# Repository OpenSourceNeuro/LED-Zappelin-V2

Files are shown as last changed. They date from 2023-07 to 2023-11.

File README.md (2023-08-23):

<p align="left">
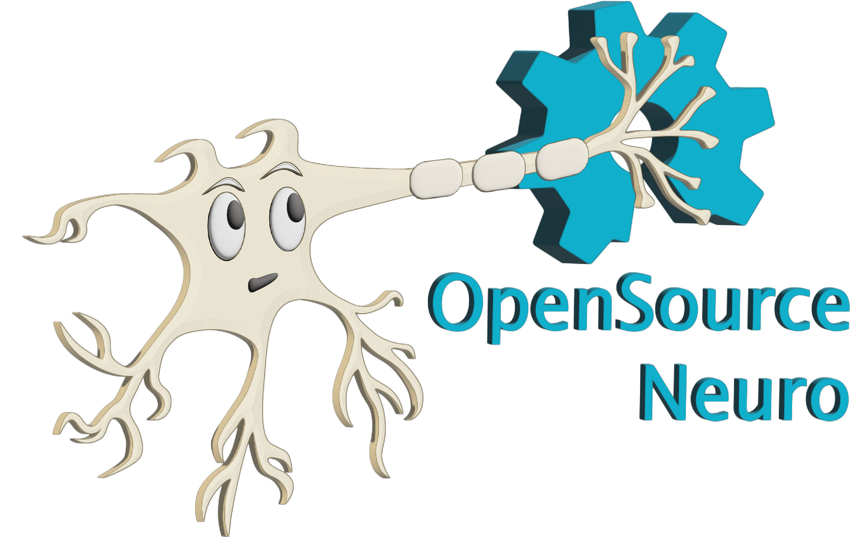
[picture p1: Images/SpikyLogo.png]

</p>

<h1 align="center"> LED Zappelin' v2</h1>
<h3 align="center">  An Open Source and versatile LED controller for arbitrary spectrum visual stimulation and optogenetics during two-photon imaging.</h3></p>
<h6 align="right">developed by M.J.Y. Zimmermann, A.M. Chagas & T. Baden</h6>

<br>

This project is licensed under the <a href="https://www.gnu.org/licenses/gpl-3.0.html">GNU General Public License v3.0</a>
<br>
The hardware is licensed under the <a href="https://cern-ohl.web.cern.ch">CERN OHL v1.2</a>

***

<p style='text-align: justify;'>
Two-photon microscopy is a cornerstone technique in neuroscience research, but combining this technology with spectrally arbitrary light stimulation can be challenging due to crosstalk between stimulation light and fluorescence detection. To overcome this limitation, we present LED Zappelin': a simple and low-cost electronic solution to rapidly time-interleave stimulation and detection epochs during scans.
</p>

The second version of this project allows user to either:

  - Independently drive up to 24 arbitrary spectrum LEDs to meet user requirements. Using the <a href="https://www.ti.com/lit/ds/symlink/tlc5947.pdf">TLC5947 LED driver</a>.
  - Control external light source generator such as the <a href="https://www.thorlabs.com/newgrouppage9.cfm?objectgroup_id=13597">Thorlabs Chrolis</a>. Using TTL logic circuits.

</br>

<p align="center">
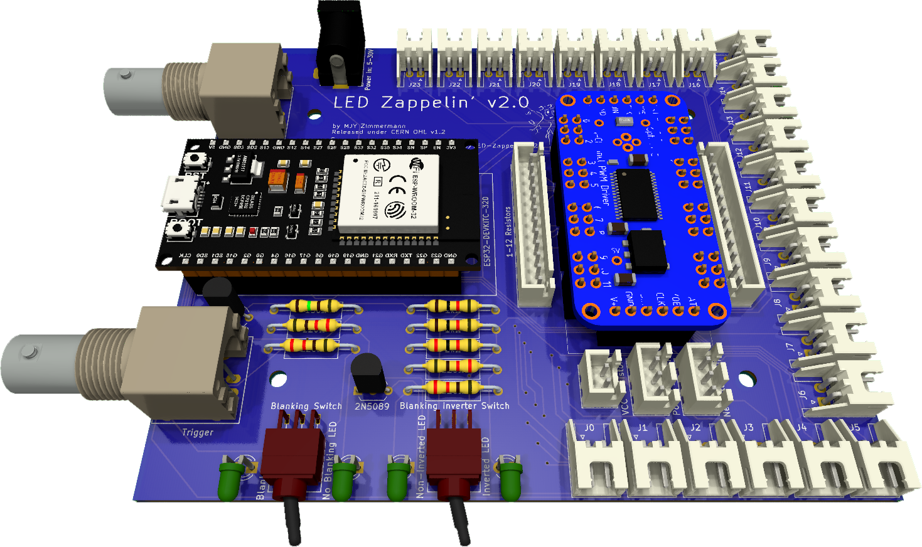
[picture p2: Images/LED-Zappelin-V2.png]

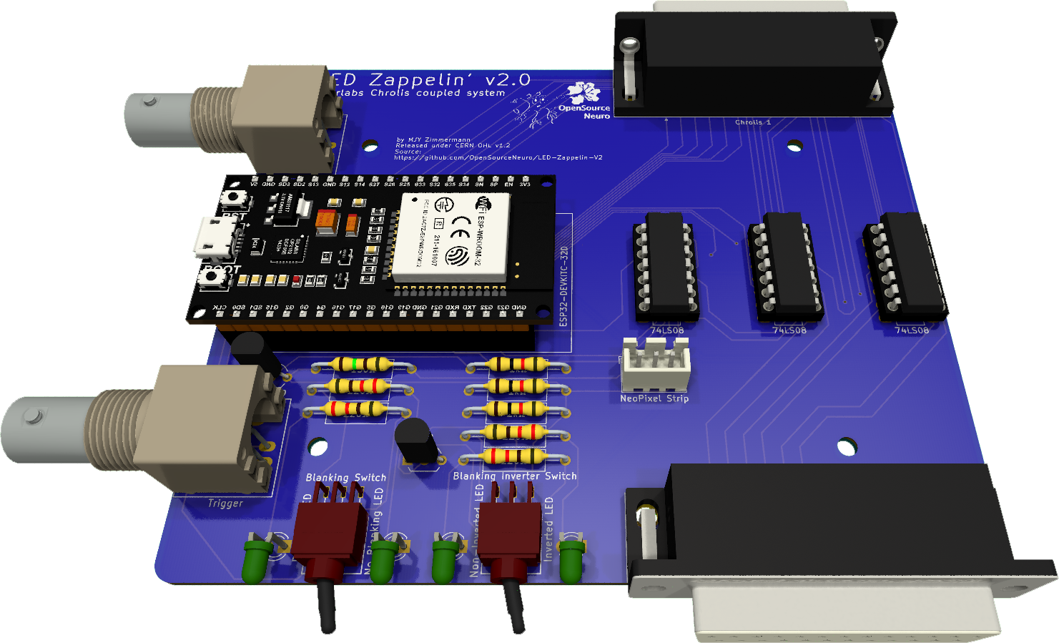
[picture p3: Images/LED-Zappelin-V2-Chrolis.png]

</p>

<h5 align="justify"> <em>Left: </em>LED Zappelin' mounted with a TLC 5947 controlling up to 24 LED channels. <em>Right: </em>LED Zappelin' mounted with TTL circuit controlling two 6-High_Power LED Chrolis systems</h5>

<br></br>

<p style='text-align: justify;'>
In the <a href=https://pubmed.ncbi.nlm.nih.gov/35498254/>original publication</a>, we demonstrate the utility of our stimulator for colour vision experiments on the in vivo tetra-chromatic zebrafish retina and for optogenetic circuit mapping in Drosophila.
</p>

<br>

- [Introduction](#Introduction)
- [BoM](https://github.com/BadenLab/LED-Zappelin/blob/master/Bills%20of%20Materials/BOM%20-%20Stimulator.csv)
- [Request a Quote]()
- [A stimulator for visual neuroscience](#Colour-Vision-Experiment)
- [A stimulator for optogenetics](#Optogenetics-Experiment)
- [A detailed assembly and instruction manual](https://github.com/BadenLab/LED-Zappelin/blob/master/Instruction%20Manual/README.md)
- [A step by step calibration script](https://github.com/BadenLab/LED-Zappelin/blob/master/Instruction%20Manual/Stimulator%20Calibration/Stimulator_Calibration.ipynb)
- [Repository Structure](#Repository-Structure)

<br>

## Introduction

<p align="justify">
Combining two-photon imaging with additional light stimulation – for example for visual stimulation or for driving optogenetic actuators – has remained challenging because the stimulation light can interfere with fluorescence detection. This can result in light artefacts in the image and/or may damage sensitive fluorescence detection equipment (e.g. photomultiplier tubes, PMTs).
</p>

<p align="justify">
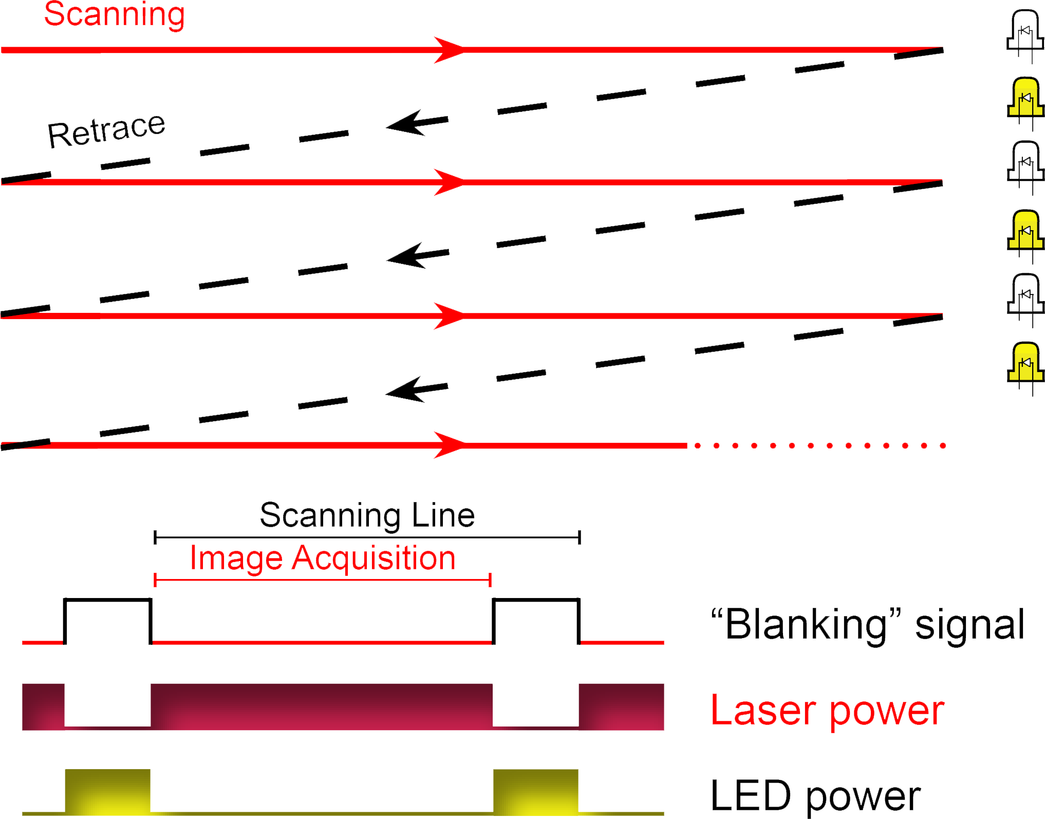
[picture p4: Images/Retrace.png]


A temporal separation between light stimulation and fluorescence detection, for example during the scan-retrace, can ameliorate these problems.
This problem can be readily solved electronically, for example through use of a microcontroller.
</p>

<br>

<p align="justify">
Here, we present such a solution. Our system can either line-synch up to 24 independent LED channels or can be connected to external commercial light sources, and can be assembled from off-the-shelf components for substantially below $200. This provides for flexible options of spectrally diverse light stimulation during two-photon scanning and comfortably provides sufficient power to drive standard optogenetics actuators such as CsChrimson.
</p>

<br>

<p align="justify">
Alongside, we also provided <a href="https://github.com/OpenSourceNeuro/LED-Zappelin-V2/tree/main/Casing%20Files">custom casing files</a> (for either 3d print or laser-cut), <a href="https://github.com/OpenSourceNeuro/LED-Zappelin-V2/tree/main/3D%20files">designed suggestions</a> for optically combining LED banks using Thorlabs parts, and an alternative 3D-printed LED holder and microscope chamber.
</p>

<p align="justify">
The device is built around an <a href="https://www.espressif.com/en/products/socs/esp32">ESP32</a>, a microcontroller which exchange signals with the recording setup, drive the light sources and runs on C++. However, users do not need to interfere with the source code as we provide an intuitive and interactive <a href="">Graphical User Interface</a> (GUI), from which all functions and variables can be manipulated.
</p>

</br>

<p align="center">
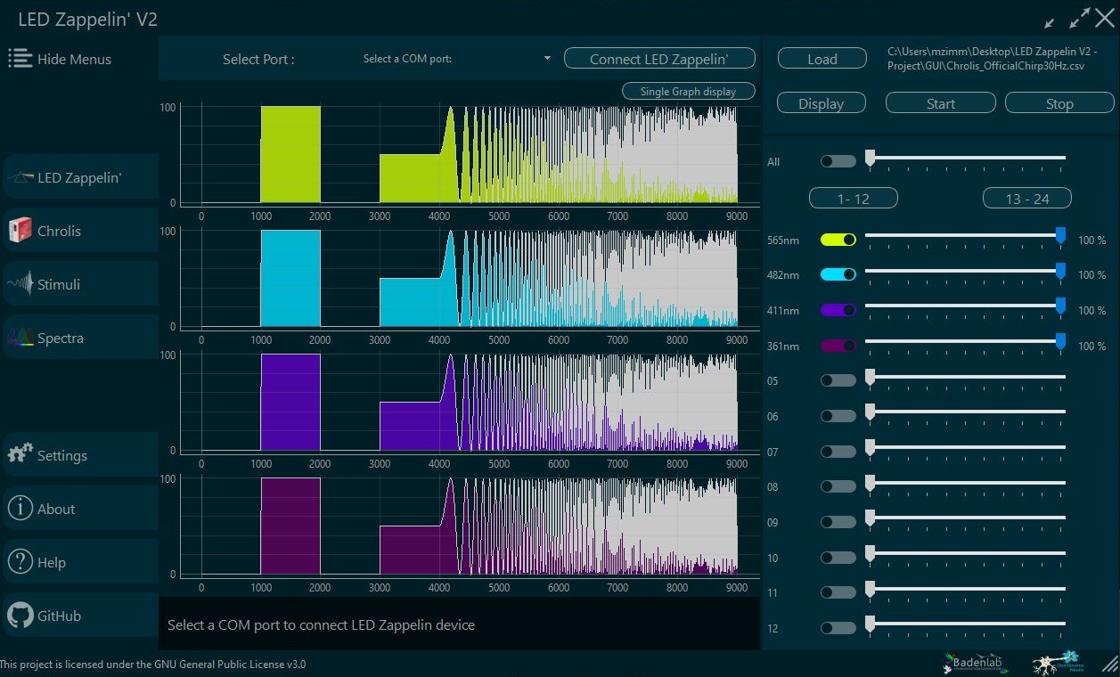
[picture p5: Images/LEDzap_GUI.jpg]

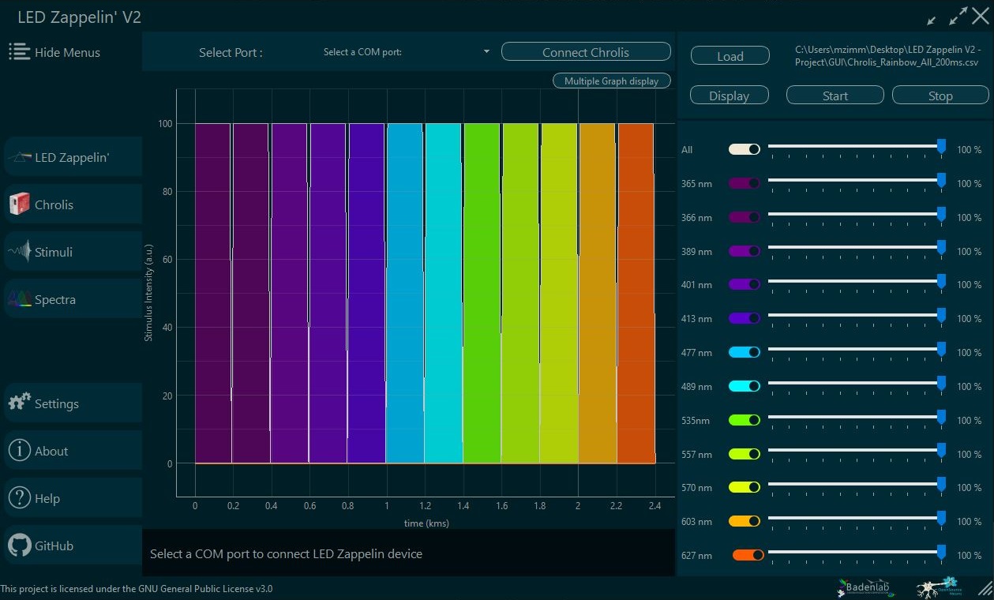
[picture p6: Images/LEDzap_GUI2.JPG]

</p>

<h5 align="justify"> <em>Left: </em>LED Zappelin' GUI controlling 4 LEDs, all executing a chirp stimulus. <em>Right: </em>LED Zappelin' controlling 12 LED channels from two Chrolis systems, executing successive On/Off stimulati</h5>

<br></br>

<p align="justify">
<a href="https://github.com/OpenSourceNeuro/LED-Zappelin-V2/blob/main/GUI_UserManual.md"><strong>Here</strong></a>, is the full user guide documentation.
</p>

<br>

***

## Colour Vision Experiment

Demo CountPages alpha (https://youtu.be/FhLoFGbbpPo)

<p align="justify">
We used LED Zappelin' for studying the retinal processing of the tetra-chromatic zebrafish retina in response to multichromatic signal.
Here we selected four LEDs that match the peak sensitivities of each cone opsins of our model.
We chose LEDs and band pass filters in such manner that the stimulating light and the detection bands do not overlap as much as possible. However a temporal separation is still necessary to avoid some overlapping and any light artefact.
</p>

</br>

<p align="center">
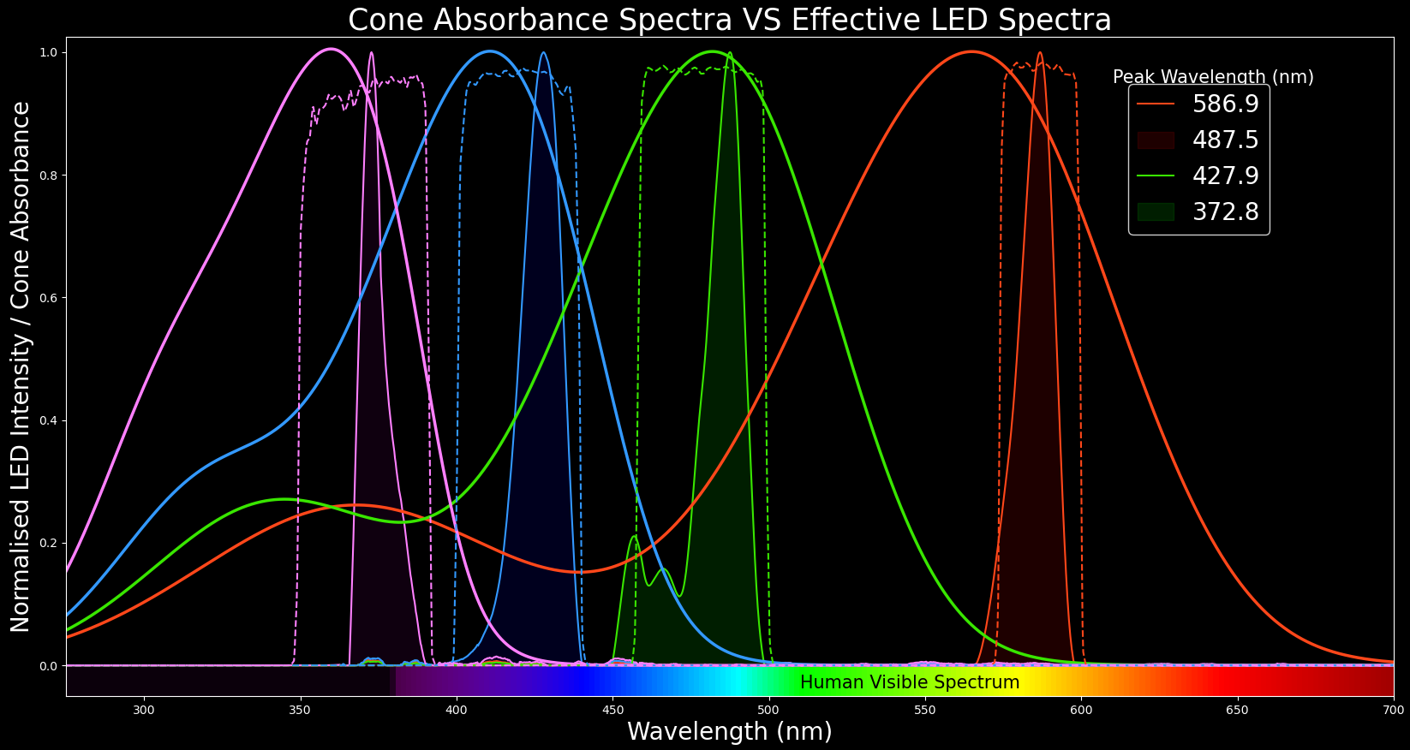
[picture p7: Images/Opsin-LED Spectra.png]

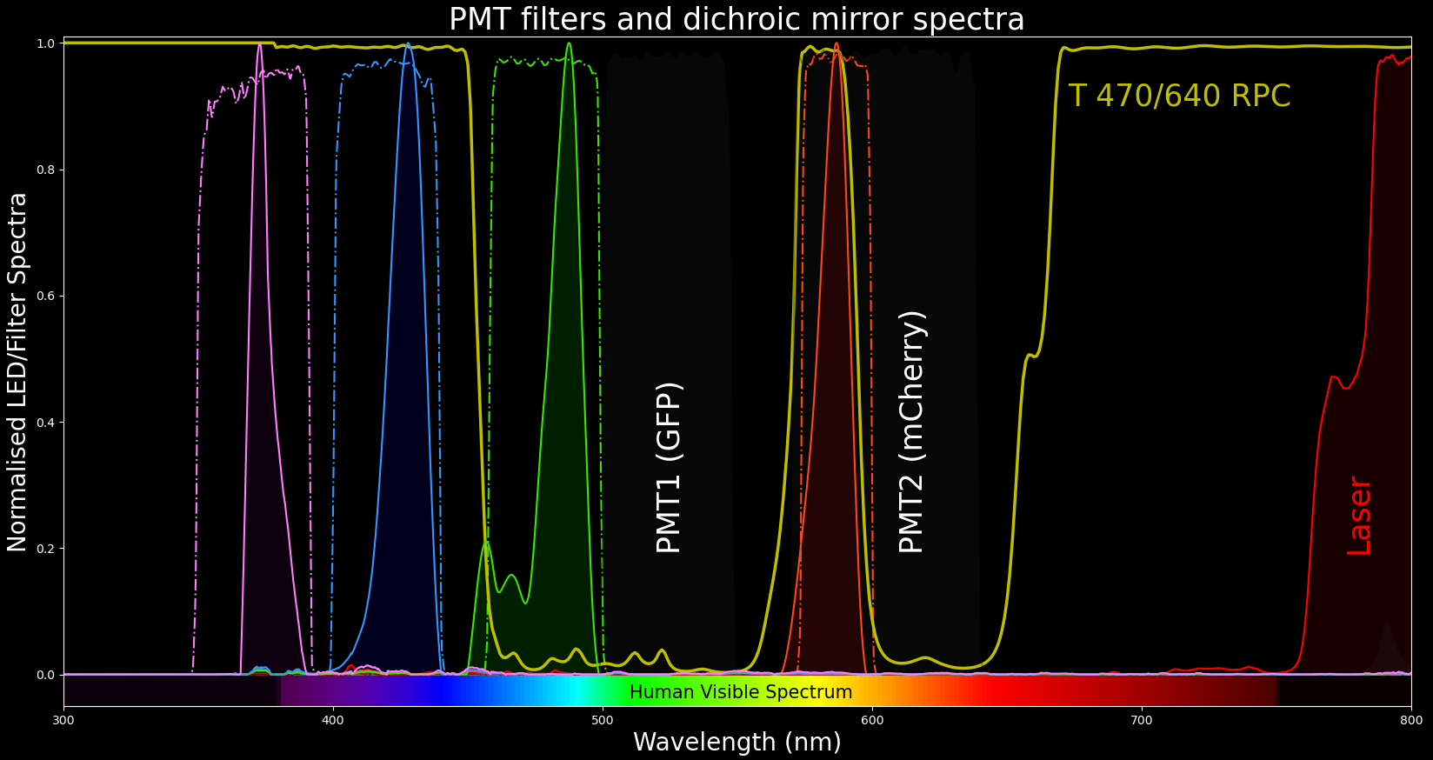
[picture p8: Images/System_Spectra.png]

</p>

<h5 align="justify"> <em>Left: </em>Zebrafish's opsin absorbance spectra overlapped with four filtered LED spectra. <em>Right: </em>The four selected stimulation LEDs along the microscope setup spectra features</h5>

<br></br>

<p align="justify">
 We recorded light-driven calcium signals under 2-photon from <a href="https://pubmed.ncbi.nlm.nih.gov/29937350/"> retinal bipolar cells in vivo in the tetra-chromatic larval zebrafish</a>. We used a transgenic line expressing a genetically encoded biosensors for calcium at the  bipolar cell synaptic terminals level (ctbp2:SyGCaMP6)  within the inner plexiform layer (IPL).
</p>

<p align="justify">
Following <a href="https://pubmed.ncbi.nlm.nih.gov/2321027/">established protocols</a>, we used a Sutter MOM microscope where light stimulation is displayed through the objective directly onto the fish retina along with the laser excitation. Fluorescence is also collected through the objective as well as from below the stage (not shown).
</p>

<p align="justify">
We presented full field steps of red, green, blue and UV light to the fish eye (respectively 567, 480, 420 and 365nm), and recorded evoked calcium signals as a readout of synaptic activity. We observed spectrally different tunings from distinct bipolar cell terminals  without detectable stimulus artefact across the scan.
</p>

<p align="center">
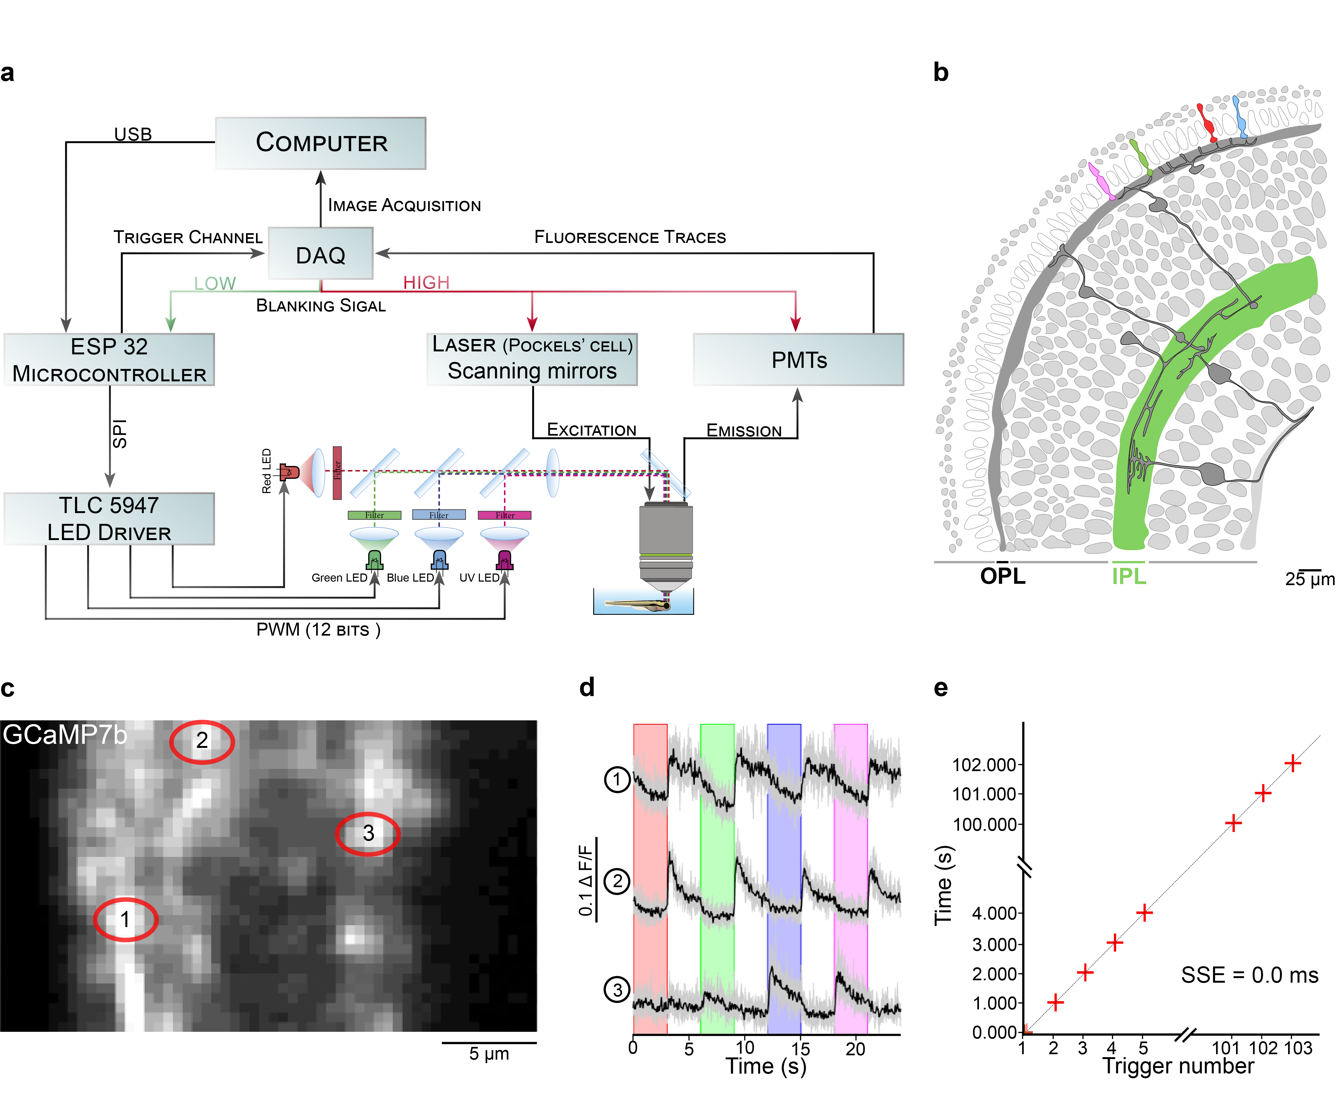
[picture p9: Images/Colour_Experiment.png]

</p>
<h5 align="justify"> a) Overview of the setup described for the visual stimulation experiment performed on the tetra-chromatic zebrafish. b) Drawing of the larval zebrafish retina highlighting the IPL. c) 2 photon scan field of the IPL with regions-of-interest marked by red circles. The 64x32 pixel image was obtained by at 1ms scan rate. d) Ca²⁺ traces (mean traces in black, n=5 trials in grey) in response to consecutive red, green, blue and UV On/Off flashes. e) Trigger timing recorded by the DAQ highlighting its accuracy over time with a precision of 0.1µs. t(n+1) = t(n) + T, where “t” is the recorded trigger time and “T” the trigger period. </5>

***

## Optogenetics Experiment

In addition to colour vision experiments, LED Zappelin' is well suited for optogenetic manipulations.

<p align="justify">
Here we illustrate this application in Drosophila larvae, were we recorded brain-wide calcium signals under 2P in response to optogenetic stimulation of all olfactory sensory neurons (OSNs).  We expressed the red-shifted channel rhodopsin CsChrimson OSNs and the genetically encoded calcium indicator GCaMP6s pan-neuronally by using larvae with the genotype: elav-Gal4;UAS-GCaMP6s/Orco-LexA;LexAOp-CsChrimson.
</p>

<p align="justify">
We placed first instar larvae under a custom-made 2P microscope in a <a href"https://github.com/OpenSourceNeuro/LED-Zappelin-V2/tree/main/3D%20files/Optogenetics%20Components">3D-printed optogenetics LED chamber</a>.
Red light stimulation was delivered from around the sides of the recording chamber and GCaMP6s fluorescence intensity was collected by two detectors one through the objective lens, and a sub-stage PMT.
We presented full field illumination steps of 615 nm light lasting 0.5 s and an inter-stimulus interval of either 3 s (b) or 10 s (c).
</p>

<p align="justify">
We observed robust stimulus-evoked activity in the primary olfactory sensory centres of the larval brain, the antennal lobes (red outlines). Similarly to colour vision experiments, we detected no light artefact.
</p>

<p align="center">
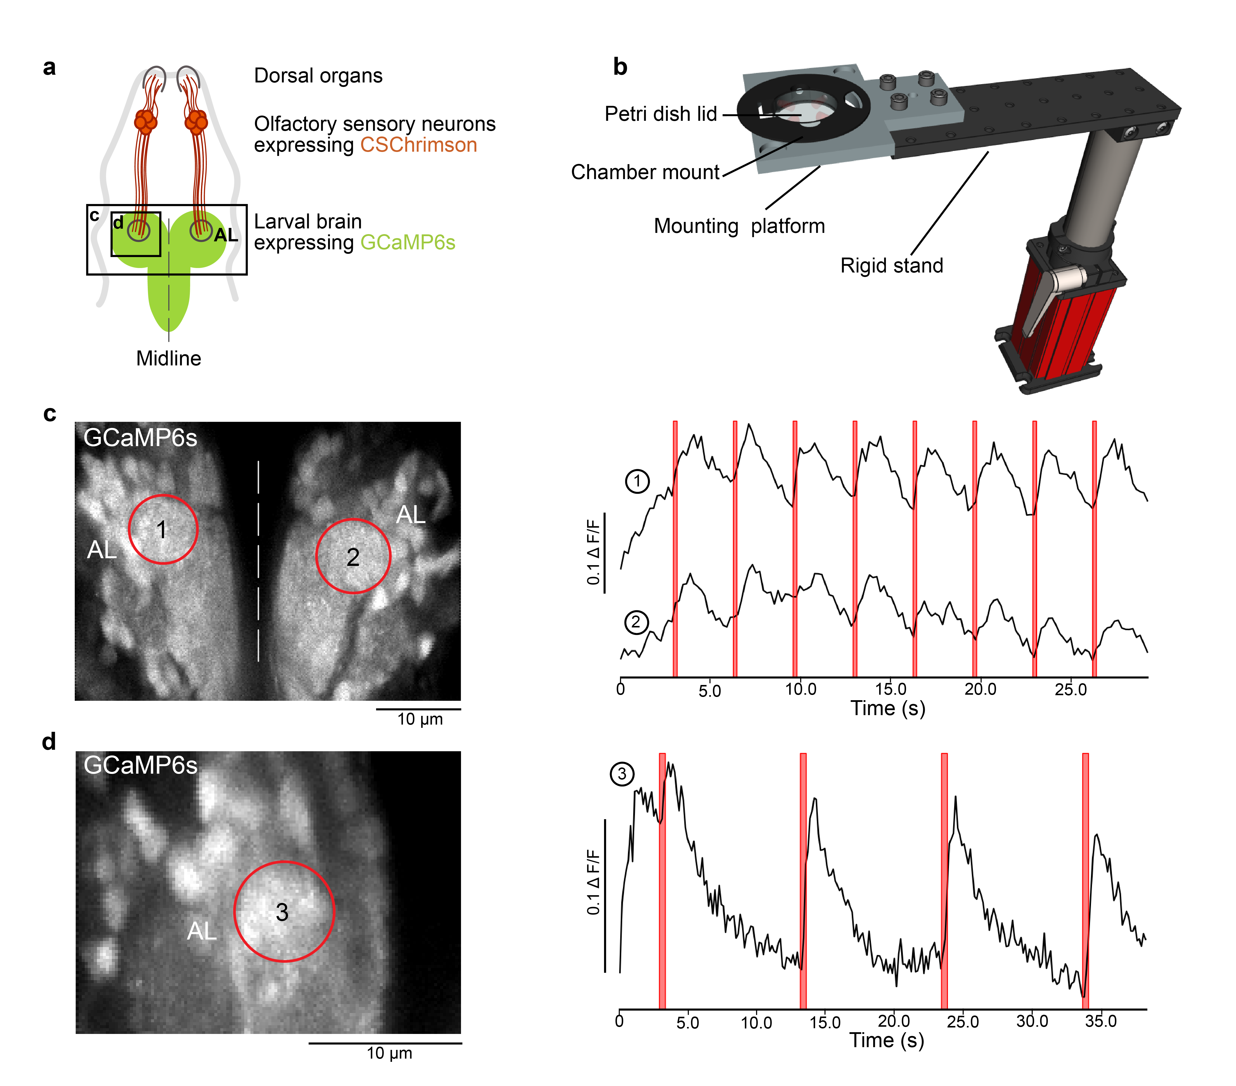
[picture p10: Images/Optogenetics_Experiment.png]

</p>
<h5 align="justify">  a) Schematic of a fruit fly first instar larval head expressing the red-shifted channel rhodopsin CsChrimson in olfactory sensory neurons and GCaMP6s in all neurons. b) Rendering of the experimental setup: The mounting chamber is placed in a 3D-printed holder, screwed onto a rigid stand (ThorLabs).  c),d)  2 photon scan field of the larval brain with antennal lobes marked by red circles (left) and Ca²⁺ traces in response to red flashes (right). c. Stimulation duration = 0.5 s, inter-stimulus interval = 3 s, image dimensions = 256 x 230, scan rate = 1081 Hz, frame rate = 4.7 Hz. d) Stimulation duration = 0.5 s, inter-stimulus interval = 10 s, image dimensions = 256 x 170, scan rate = 1077Hz, frame rate = 6.34 Hz. </h5>

***
## Repository structure (to be updated)

```
├───3D Designs                                Contains printed parts for the stimulator and optical components
│   ├───Optical Components
|   |   ├───STL renderings                    - Printing files
|   |   └───SCAD files                        - SCAD files to be modified if need be
│   ├───Optogenetics Components
|   |   ├───STL renderings                    - Printing files
|   |   └───SCAD files                        - SCAD files to be modified if need be
│   └───Stimulator
|       ├───STL renderings                    - Printing files
|       └───SCAD files                        - SCAD files to be modified if need be
|
├───Arduino Code                              Stimulator Code
|   ├───Stimulator Code                       - Adaptable C+ code for running the stimulator
|   └───LED driver library                     - Library to run the TLC 5947
|
├───Bill of Materials                         List of necessary components and retailer suggestions
|
├───Datasheets                                - Contains all technical sheet for:
|   ├───Optical Components                    - ...LEDs, Filters, Dichroic Mirrors used in the presented example
|   ├───Stimulator                            - ...micro-controller and LED driver
|   └───Spectrometer                          - ...device used for calibration
|
├───Images                                    Image repository
|
├───Instruction Manual                        Detailed manual to assemble and calibrate the stimulator
|   └───Stimulator Calibration                - Contains calibration recordings and the adaptable jupyter notebook script to calibrate the stimulator
|       ├───Arduino Calibration Code          - Sequence used for the calibration
|       ├───Calibration Figures               - Illustration from calibration measurements
|       ├───Filters                           - Filters and dicroic mirrors spectra
|       ├───Powermeter Recording              - Recording of the calibration sequence
|       ├───Spectrometer Recording            - Recording of the calibration sequence
|       └───Stimulator Calibration            - iPython Jupyter Notebook script for calibration
|
├───PCB                                       KiCad and Gerber files to modified and generate PCB for:
│   ├───Potentiometer mounts                  - ...trimmer potentiometers that set the LED maximum brightness
│   └───Stimulator                            - ...the stimulator itself
|
└───References                                Publication used to design and conceive this model

```

***



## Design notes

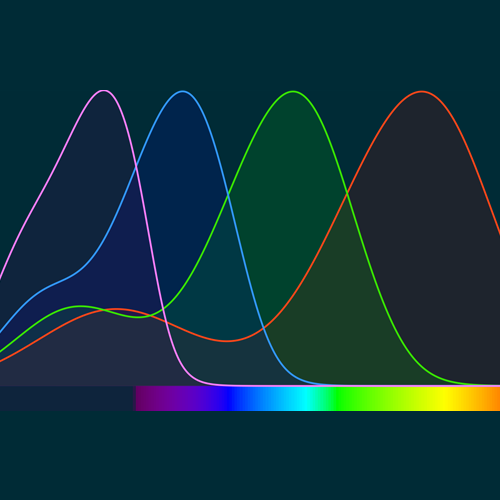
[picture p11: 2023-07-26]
GUI/resources/Spectra.png

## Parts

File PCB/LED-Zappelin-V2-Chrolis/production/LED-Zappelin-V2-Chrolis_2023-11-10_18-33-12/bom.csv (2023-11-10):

Designator | Footprint | Quantity | Value | LCSC Part #
D1 | LED_D3.0mm | 1 | Blanking LED
D2 | LED_D3.0mm | 1 | No Blanking LED
D3 | LED_D3.0mm | 1 | Inverted LED
D4 | LED_D3.0mm | 1 | Non-Inverted LED
H1, H2, H3, H4 | MountingHole_3mm | 4 | MountingHole
J1 | BNC_Socket_TYCO-AMP_LargePads | 1 | Blanking Signal
J2 | BNC_Socket_TYCO-AMP_LargePads | 1 | Trigger
J3 | DSUB-25_Female_Horizontal_P2.77x2.84mm_EdgePinOffset9.90mm_Housed_MountingHolesOffset11.32mm | 1 | Chrolis 1
J4 | DSUB-25_Female_Horizontal_P2.77x2.84mm_EdgePinOffset9.90mm_Housed_MountingHolesOffset11.32mm | 1 | Chrolis 2
J5 | JST_XH_B3B-XH-A_1x03_P2.50mm_Vertical | 1 | NeoPixel Strip
J6 | BarrelJack_Horizontal | 1 | Barrel_Jack
Q1, Q2 | TO-92L_Inline_Wide | 2 | 2N5089
R1, R6 | R_Axial_DIN0309_L9.0mm_D3.2mm_P15.24mm_Horizontal | 2 | 1kΩ
R10 | R_Axial_DIN0309_L9.0mm_D3.2mm_P15.24mm_Horizontal | 1 | 330
R2 | R_Axial_DIN0309_L9.0mm_D3.2mm_P15.24mm_Horizontal | 1 | 2kΩ
R3, R4, R7, R8 | R_Axial_DIN0309_L9.0mm_D3.2mm_P15.24mm_Horizontal | 4 | 220Ω
R5 | R_Axial_DIN0309_L9.0mm_D3.2mm_P15.24mm_Horizontal | 1 | 150Ω
R9 | R_Axial_DIN0309_L9.0mm_D3.2mm_P15.24mm_Horizontal | 1 | 1k
SW1 | maxi_DPDT_Angled | 1 | Blanking Switch
SW2 | maxi_DPDT_Angled | 1 | Blanking Inverter Switch
U1 | MODULE_ESP32-DEVKITC-32D | 1 | ESP32-DEVKITC-32D
U2, U3, U4 | DIP-14_W7.62mm_LongPads | 3 | 74LS08
U5 | TO-220-3_Vertical | 1 | LM317_TO-220

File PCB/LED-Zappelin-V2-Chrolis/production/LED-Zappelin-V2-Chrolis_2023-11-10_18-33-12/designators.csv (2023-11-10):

:1
D1:1
D2:1
D3:1
D4:1
H1:1
H2:1
H3:1
H4:1
J1:1
J2:1
J3:1
J4:1
J5:1
J6:1
Q1:1
Q2:1
R1:1
R10:1
R2:1
R3:1
R4:1
R5:1
R6:1
R7:1
R8:1
R9:1
SW1:1
SW2:1
U1:1
U2:1
U3:1
U4:1
U5:1

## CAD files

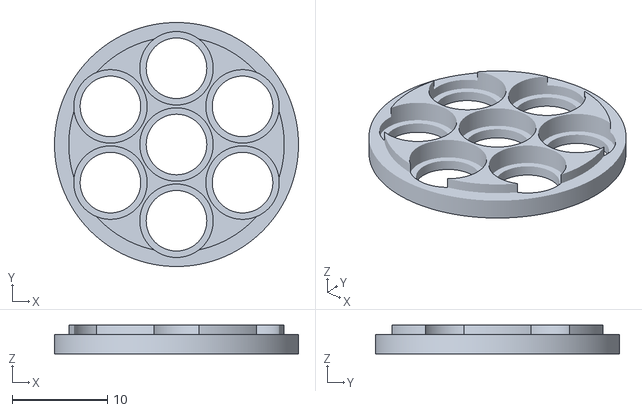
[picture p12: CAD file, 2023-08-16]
3D files/Optical Components/STL Files/7_LED_Holder.stl
25.6 x 25.6 x 3.00

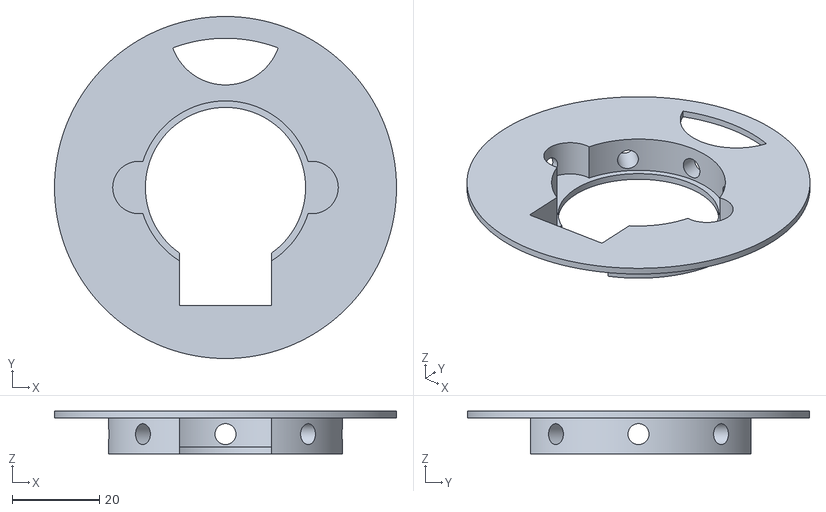
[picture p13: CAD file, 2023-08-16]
3D files/Optogenetics Components/STL Files/OptoChamber - Petri dish version.stl
78.4 x 78.4 x 9.75

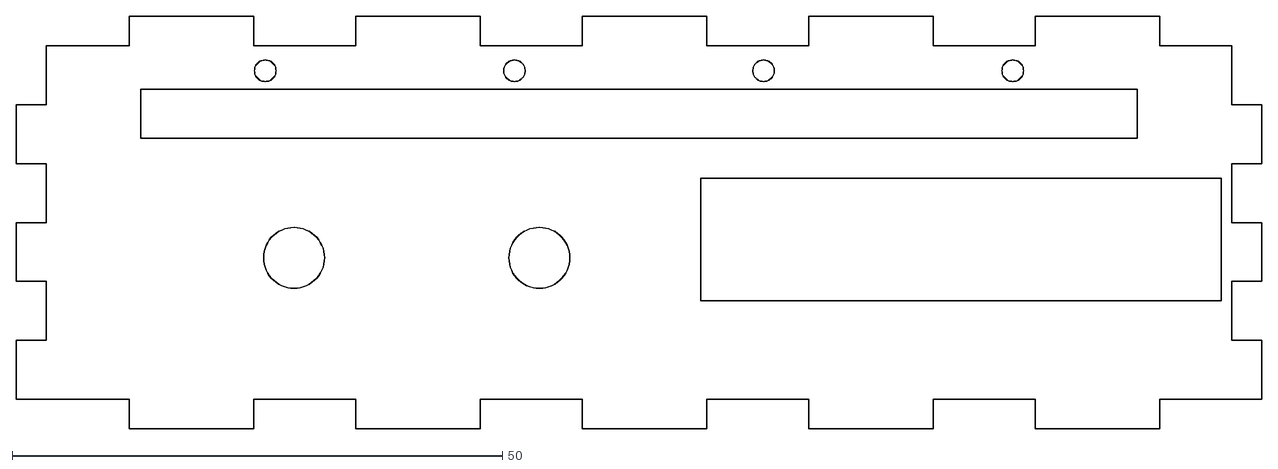
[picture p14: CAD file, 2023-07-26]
Casing Files/LED-Zappelin V2 - Chrolis/DXF/Front.dxf
127.0 x 42.0

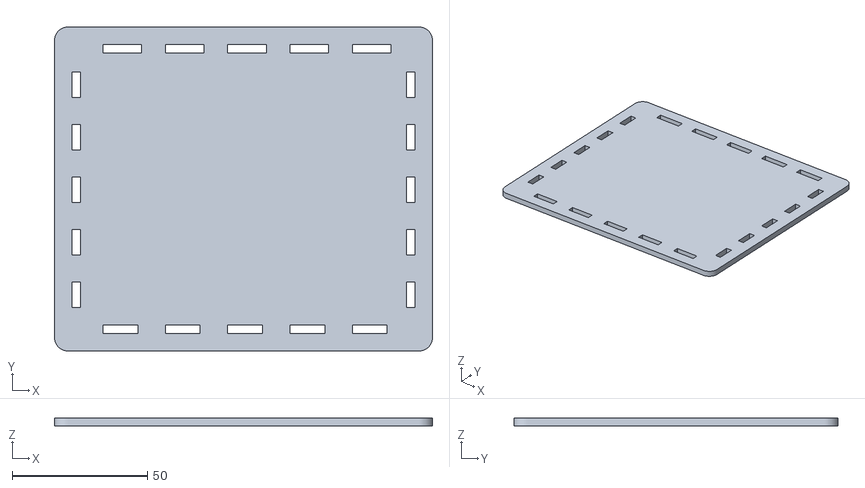
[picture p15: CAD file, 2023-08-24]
Casing Files/LED-Zappelin V2 - Chrolis/STL/LED-Zappelin V2 - Chrolis_Top.stl
140.0 x 120.0 x 3.00

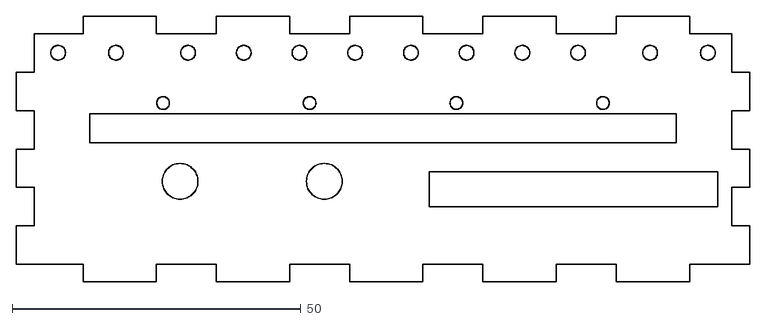
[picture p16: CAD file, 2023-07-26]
Casing Files/LED-Zappelin V2/DXF/LED-Zappelin V2_Front.dxf
127.0 x 46.0

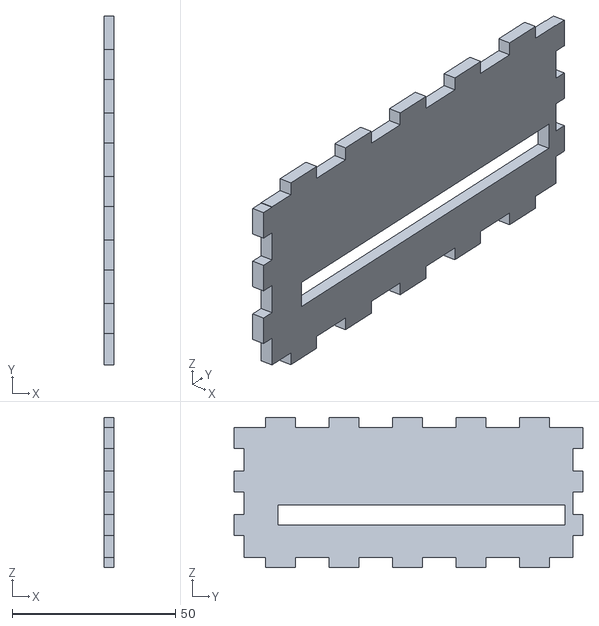
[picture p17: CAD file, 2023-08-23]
Casing Files/LED-Zappelin V2/STL/LED-Zappelin_Right.stl
3.00 x 107.0 x 46.0

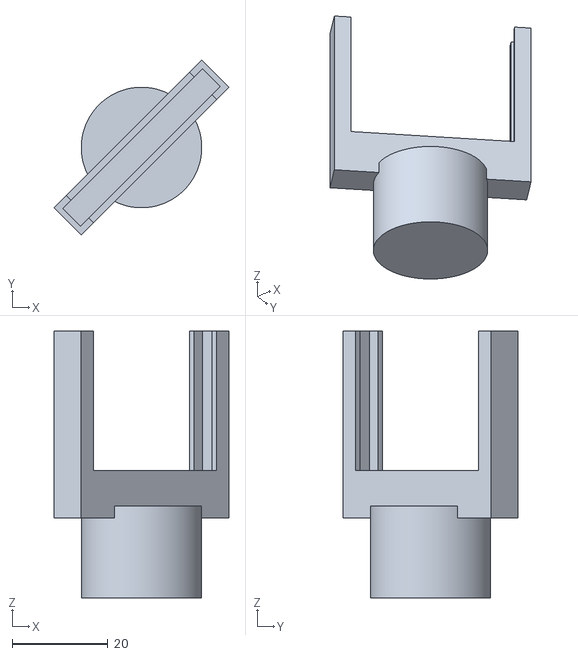
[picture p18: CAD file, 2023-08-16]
3D files/Optical Components/STL Files/dichroic_holder.stl
36.6 x 36.6 x 55.9

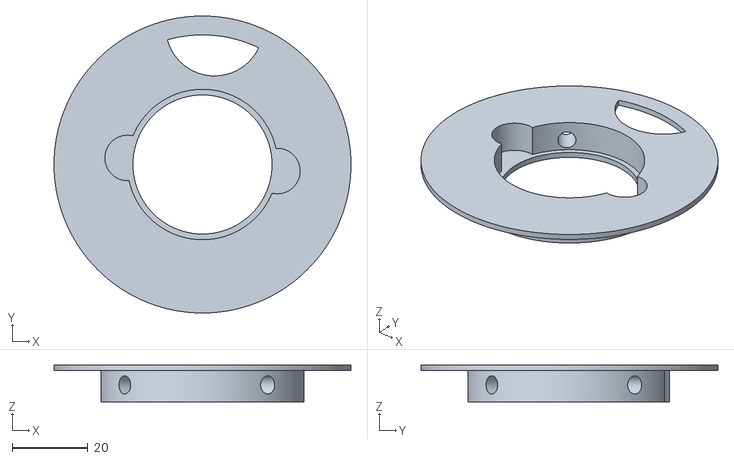
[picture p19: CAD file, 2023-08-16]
3D files/Optogenetics Components/STL Files/OptoChamber - RC-40HP version.stl
78.4 x 78.4 x 9.75

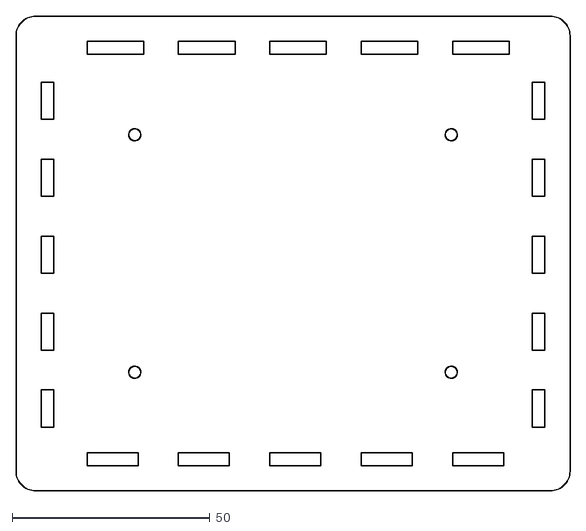
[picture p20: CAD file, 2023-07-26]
Casing Files/LED-Zappelin V2 - Chrolis/DXF/Bottom.dxf
140.0 x 120.0

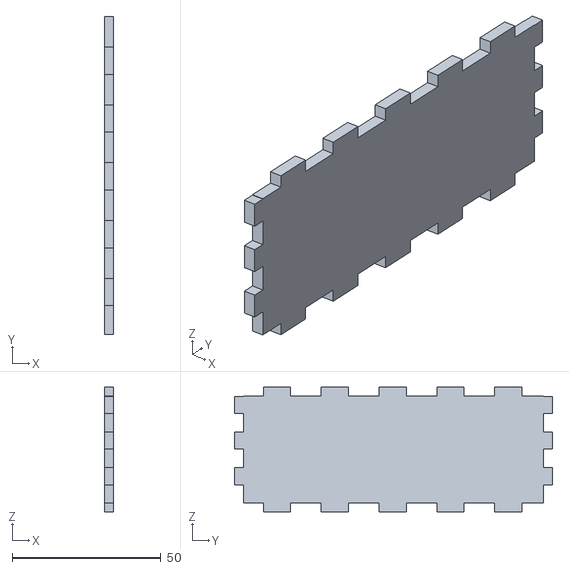
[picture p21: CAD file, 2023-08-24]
Casing Files/LED-Zappelin V2 - Chrolis/STL/LED-Zappelin V2 - Chrolis_Right.stl
3.00 x 107.0 x 42.0

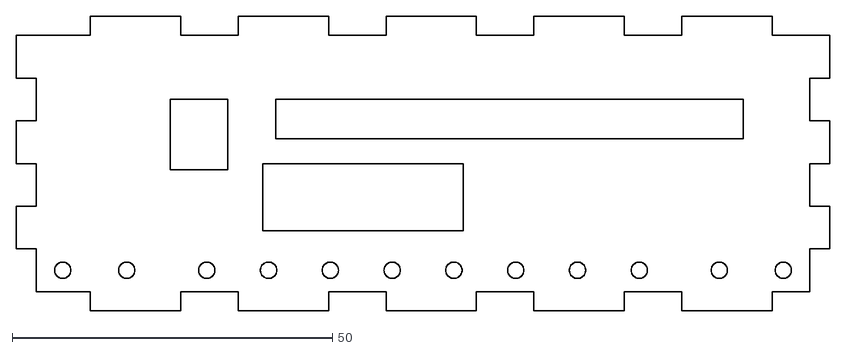
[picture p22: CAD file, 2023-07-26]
Casing Files/LED-Zappelin V2/DXF/LED-Zappelin V2_Back.dxf
127.0 x 46.0

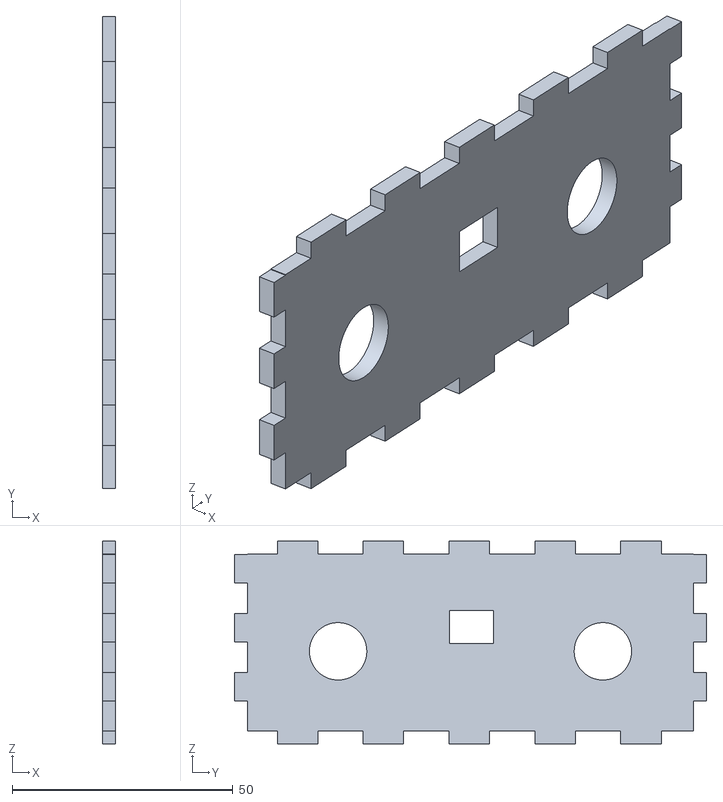
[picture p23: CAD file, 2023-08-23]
Casing Files/LED-Zappelin V2/STL/LED-Zappelin_Left.stl
3.00 x 107.0 x 46.0

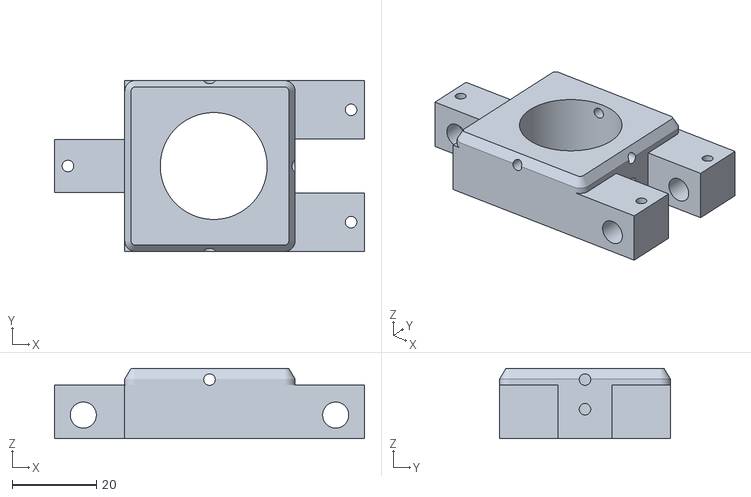
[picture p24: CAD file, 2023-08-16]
3D files/Optical Components/STL Files/LCP30 - modified.stl
73.7 x 40.6 x 16.7

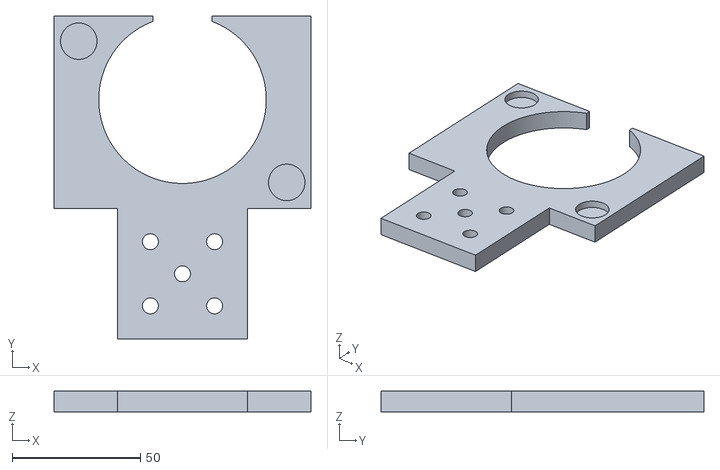
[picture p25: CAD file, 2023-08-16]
3D files/Optogenetics Components/STL Files/OptoChamber - Plaform mount.stl
100.0 x 125.8 x 8.00

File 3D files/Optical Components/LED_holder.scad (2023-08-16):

/* 
                 LED Holder design to fit into a Thorlab 1 inch diameter lens holder
                            
        This holder has been designed to fit into the stimulator described in:
        LED Zappelin' v2.2: An opensource LED stimulator for visual and optogenetics 
        stimulation in combination with 2-photon recording

This project is Open Source licensed, released under CERN OHL v1.2

by M.J.Y. Zimmermann, 2018.12.11
Baden Lab, CRPC, School of Life Sciences, University of Sussex, United Kingdom



// // // // // // // // // // // // // // // // // // // // // // // // // // // // //
/*                            ---  User Parameters  ---                             */

Wall = 2;           // Defines the wall thickness of the box
Smoothness = 360;   // Number of facets
tol = 0.1;          // Printing tolerance

// // // // // // // // // // // // // // // // // // // // // // // // // // // //
/*                               ---  Switches  ---                              */

n_LED = 1;          // Determine the number of LEDs to mount (from 1 to 7)


// // // // // // // // // // // // // // // // // // // // // // // // // // // //
// // // // // // // // // // // // // // // // // // // // // // // // // // // //
/*                        ---  Component Parameters  ---                        */

r_lens_1_inch    = 25.8/2;      // ThorLabs 1 inch diameter lens radius
r_inner_ring     = 22.8/2;      // ThorLabs 1 inch diameter lens ring radius
h_ring           = 2;           // ThorLabs 1 inch diameter lens ring heigh

r_LED            = 6.35/2;      // 5mm LED radius
h_LED_Holder     = 3;
d_LED_Holder     = 8;           // 5mm LED clip diameter
h_clip           = 1;           // inside 5mm LED clip heigh
r_Clip           = 7.5/2+tol;   // 5mm LED clip radius



// // // // // // // // // // // // // // // // // // // // // // // // // // // //
/*                               ---  Display  ---                               */

difference(){
    LED_holder();
    
    if (n_LED==1){
        LED_hole();
    }
    if (n_LED==2){
        for (a=[0:180:360])rotate([0,0,a])translate([0,7,0])LED_hole();
    }
    if (n_LED==3){
        for (a=[0:360/3:360])rotate([0,0,a])translate([0,d_LED_Holder,0])LED_hole();
    }
    if (n_LED==4){
        LED_hole();
        for (a=[0:360/3:360])rotate([0,0,a])translate([0,d_LED_Holder,0])LED_hole();
    }
    if (n_LED==5){
        LED_hole();
        for (a=[0:360/4:360])rotate([0,0,a])translate([0,d_LED_Holder,0])LED_hole();
    }
    if (n_LED==6){
        LED_hole();
        for (a=[0:360/5:360])rotate([0,0,a])translate([0,d_LED_Holder,0])LED_hole();
    }
    if (n_LED==7){
        LED_hole();
        for (a=[0:360/6:360])rotate([0,0,a])translate([0,d_LED_Holder,0])LED_hole();
    }
}


// // // // // // // // // // // // // // // // // // // // // // // // // // // //
/*                               ---  Modules  ---                               */

module LED_holder(){
    difference(){
        cylinder(r=r_lens_1_inch-tol, h=h_LED_Holder, $fn=Smoothness);
    
        translate([0,0,h_ring])difference(){
            cylinder(r=r_lens_1_inch, h=h_LED_Holder, $fn=Smoothness);
            cylinder(r=r_inner_ring-tol, h=h_LED_Holder, $fn=Smoothness);
        }
    } 
}

module LED_hole(){
    cylinder(r=r_LED, h=h_LED_Holder, $fn=Smoothness);
    translate([0,0,h_clip])cylinder(r=r_Clip,h=h_LED_Holder,$fn=Smoothness);
}

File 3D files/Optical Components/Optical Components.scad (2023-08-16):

/* 

                            Optical Component parts for
                            LED Zappelin' v2.2.
                    
        An opensource LED stimulator for visual and optogenetics stimulation in combination with 2-photon recording



This 3D file is designed to be used along ThorLabs optical cage assemblies 

Source : https://github.com/BadenLab/LED-Zappelin
This project is Open Source licensed, released under CERN OHL v1.2

by M.J.Y. Zimmermann and A.M. Chagas, 2019.02.25
Baden Lab, CRPC, School of Life Sciences, University of Sussex, United Kingdom

                                                                                     */


// // // // // // // // // // // // // // // // // // // // // // // // // // // // //
/*                            ---  User Parameters  ---                             */

Smoothness = 360;        // Number of facets. A value of 360 is recommended for a smooth print
tol = 0.1;               // Tolerance value, set by default to 0.1 for Ultimaker2 printer
Wall = 2.5;              // Wall thickness (applied only to certain modules)
wall = 2;                // Wall thickness (applied only to certain modules

// // // // // // // // // // // // // // // // // // // // // // // // // // // //
// // // // // // // // // // // // // // // // // // // // // // // // // // // //
/*                               ---  Switches  ---                              */
        LCP30 = 1;
        Mirror_Holder = 1;
        Dichroic_Frame = 1;


// // // // // // // // // // // // // // // // // // // // // // // // // // // // //
/*                         ---  Display Parameters  ---                             */

rotation = 45;      // mirror angle 
lens_offset = 1;
sep = 5;            // Separtion between objects (75 by default for proper display)


// // // // // // // // // // // // // // // // // // // // // // // // // // // //
// // // // // // // // // // // // // // // // // // // // // // // // // // // //
/*                        ---  Component Parameters  ---                        */

rod_pos2 = 60/2;         // Rod position for 60mm cage system
r_rod = 6.1/2 + tol/2;   // Rod radius 0.25 inch
S4 = 2.75/2;             // ThorLabs small holding screws 0.05 inch
r_lens_1_inch = 25.4/2;  // ThorLabs 1 inch Lens

Frame_Base = 10;
dichz = 25.4;
dichy = 1;
dichx = 36.2;

x_Frame = 36.2;
y_Frame = 3;
z_Frame = 25.4+1.5*Wall;
X_LCP30 = 73.7; //outer cube length
x_LCP30 = 40.7; //inner cube length
y_LCP30 = 40.6;
z_LCP30 = 12.70; //module thickness
y_Groove_LCP30 = 12.9;
x_arm_LCP30 = 16.5; //arm width
y_arm_LCP30 = 14; //arm length
x_ext_LCP30 = 96.3; //module diagonal length
pos_z_Screw_LCP30 = 5.6;
pos_x_screw_LCP30 = 67.3/2;
pos_y_screw_LCP30 = 26.7/2;

h_add=4;


 // // // // // // // // // // // // // // // // // // // // // // // // // // // //
/*                               ---  Display  ---                               */
if (LCP30==1){LCP();}
if (Mirror_Holder==1){translate([lens_offset,0,sep])rotate([0,0,rotation])mirror_holder();}
if (Dichroic_Frame==1){translate([lens_offset,0,z_LCP30+h_add+Frame_Base+2*sep])rotate([0,0,rotation])dich_frame();}


// // // // // // // // // // // // // // // // // // // // // // // // // // // //
/*                               ---  Modules  ---                               */

module LCP(){
difference(){
        union(){
            translate([-X_LCP30/2,-y_LCP30/2,0])cube([X_LCP30,y_LCP30,z_LCP30]);
             minkowski(){
                translate([-x_LCP30/2+2*tol+Wall,-y_LCP30/2+Wall,z_LCP30])cube([x_LCP30-2*tol-2*Wall,y_LCP30-2*Wall,h_add-Wall]);
                cylinder(r1=Wall,h=Wall,$fn=Smoothness);
            }
        }
        
        difference(){
           translate([-X_LCP30/2,-y_Groove_LCP30/2,0])cube([X_LCP30,y_Groove_LCP30,z_LCP30]);
           translate([-x_LCP30/2,-y_LCP30/2,0])cube([x_LCP30,y_LCP30,z_LCP30]);
        }
        
        Screw_LCP30();
        translate([lens_offset,0,0])cylinder(r=r_lens_1_inch,h=z_LCP30+h_add,$fn=Smoothness);
        
        //customisation
        translate([-X_LCP30/2,-y_LCP30/2,0])cube([X_LCP30/2-x_LCP30/2+2*tol,y_LCP30,z_LCP30]);
    }
    //customization
    difference(){
        
        translate([-X_LCP30/2,-y_Groove_LCP30/2+2*tol,0])cube([X_LCP30/2-x_LCP30/2+2*tol,y_Groove_LCP30-4*tol,z_LCP30]);
        
        Screw_LCP30();
        translate([-pos_x_screw_LCP30,0,0])cylinder(r=S4,h=z_LCP30,$fn=Smoothness);
    }
}

module Screw_LCP30(){ 
    translate([pos_x_screw_LCP30,pos_y_screw_LCP30,0])cylinder(r=S4,h=z_LCP30,$fn=Smoothness);
    translate([pos_x_screw_LCP30,-pos_y_screw_LCP30,0])cylinder(r=S4,h=z_LCP30,$fn=Smoothness);
    
    translate([rod_pos2,-y_LCP30/2,pos_z_Screw_LCP30])rotate([-90,0,0])cylinder(r=r_rod,h=y_LCP30,$fn=Smoothness);
    translate([-rod_pos2,-y_LCP30/2,pos_z_Screw_LCP30])rotate([-90,0,0])cylinder(r=r_rod,h=y_LCP30,$fn=Smoothness);
    
    
    translate([x_LCP30/2,0,z_LCP30+h_add/3])rotate([0,-90,0])cylinder(r=S4,h=x_LCP30/2,$fn=Smoothness);
    translate([x_LCP30/2,0,h_add+3])rotate([0,-90,0])cylinder(r=S4,h=x_LCP30/2,$fn=Smoothness);
    translate([0,x_LCP30/2,z_LCP30+h_add/3])rotate([90,0,0])cylinder(r=S4,h=x_LCP30/2,$fn=Smoothness);
    translate([0,-x_LCP30/2,z_LCP30+h_add/3])rotate([-90,0,0])cylinder(r=S4,h=x_LCP30/2,$fn=Smoothness);
}

module mirror_holder(){
cylinder(r=r_lens_1_inch-tol,h=z_LCP30+Wall+h_add,$fn=Smoothness);
    
translate([0,0,z_LCP30+h_add])difference(){
    translate([-x_Frame/2-1.5*Wall,-y_Frame/2-Wall,0])cube([x_Frame+3*Wall,y_Frame+2*Wall,z_Frame+Frame_Base]);
    
    translate([-x_Frame/2-tol,-y_Frame/2-Wall,Frame_Base])cube([x_Frame+2*tol,y_Frame+2*Wall,z_Frame+tol]);
    translate([-x_Frame/2-Wall-tol,-y_Frame/2-wall/2-tol,Frame_Base-Wall/2])cube([x_Frame+2*Wall+2*tol,y_Frame+wall+2*tol,z_Frame+Wall/2+tol]);
}
}

module dich_frame(){
difference(){    
    translate([-x_Frame/2-Wall,-y_Frame/2-wall/2,0])cube([x_Frame+2*Wall,y_Frame+wall,z_Frame]);

    translate([-dichx/2-tol,-y_Frame/2-wall/2,Wall-tol])cube([dichx+2*tol,dichy+wall/2,dichz+2*tol]);
    translate([-dichx/2+wall/2,-y_Frame/2-Wall,Wall-tol+wall/2])cube([dichx-wall,y_Frame+2*wall,dichz-wall]);
    translate([-Wall,-y_Frame/2-wall/2,z_Frame-Wall])cube([2*wall,dichy+wall/2,Wall]);
}
}

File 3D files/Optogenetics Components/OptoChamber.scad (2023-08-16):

/* 

                            Opto Chamber v1.1
                            
    
 
This 3D file is designed for the Multi-Chromatic Stimulator project components and its customed PCB
Source : https://github.com/BadenLab/LED-Zappelin
This project is Open Source licensed, released under CERN OHL v1.2

by Tom Baden
modified by MJY Zimmermann
Baden Lab, CRPC, School of Life Sciences, University of Sussex, United Kingdom, www.badenlab.org 

and Sinziana Pop
Prieto Lab, Francis Crick Institute, United Kingdom
                                                                                     */


// // // // // // // // // // // // // // // // // // // // // // // // // // // // //
/*                            ---  User Parameters  ---                             */

tol = 0.1;                // Printing tolerance
wall = 1.5;               // Defines the wall thickness of the chamber
Smoothness = 30;         // Number of facets


// // // // // // // // // // // // // // // // // // // // // // // // // // // //
// // // // // // // // // // // // // // // // // // // // // // // // // // // //
/*                               ---  Switches  ---                              */

Version = 2;              // Select either version 1 or 2, or enter 0 for no display
Platform = 1;             // Enter 1 for displaying the mounting platform, 0 to hide it


// // // // // // // // // // // // // // // // // // // // // // // // // // // //
// // // // // // // // // // // // // // // // // // // // // // // // // // // //
/*                        ---  Component Parameters  ---                        */

thickwall = 7;            // Inner circle thickness
Asub_r = 39.5/2 + tol;    // Petri dish hole radius 
R_Accessgroove = 6;       // Access groove radius

A_h= wall;                // Chamber heigh
A_r = 39.2;               // Chamber radius
A_h2= 9;                  // Inner circle heigh
A_r2= Asub_r + thickwall; // Inner circle radius

A_LED_r = 2.3 + tol;      // LED holder radius
A_LED_zpos = A_h2-4.5;    // LED holder heigh position

Olf_width = 21;           // Width for the olfactory system

mount_width = 50.8;       // Platform width
stage_depth = 8;          // Stage height
stage_width = 100;        // Stage width
stage_length = 75;        // Stage length


rect_hole_width = 23;
rect_hole_length = 100;
rect_hole_y = 70;

circ_hole_rad = 32.5+tol;

screw_rad = 6/2+tol;
screw_coord1 = 12.9;
screw_coord2 = 37.9;


magnet_rad = 14/2+tol;    // Mounting magnet radius
magnet_depth = 3+tol;     // Mounting magnet height

magnet1_x = -15;          // First magnet x_position
magnet1_y = 116;          // First magnet y_position

magnet2_x = 66;           // Second magnet x_position
magnet2_y = 61;           // Second magnet y_position



 // // // // // // // // // // // // // // // // // // // // // // // // // // // //
/*                               ---  Display  ---                               */

if (Version==1){rotate([0,0,40])
    difference(){ 
        A();
        Asub(); 
    }
    difference(){ 
        B();
        Bsub(); 
    }
}
 
if (Version==2){rotate([0,0,45])
    difference(){ 
        A2();
        A2sub(); 
    }   
    difference(){ 
        B2();
        B2sub(); 
    }
}

if (Platform==1){
    translate([-25,-90,-9])stage();
}


// // // // // // // // // // // // // // // // // // // // // // // // // // // //
/*                               ---  Modules  ---                               */

module A() {
	translate([0,0,0])rotate([0,0,0])cylinder($fn=Smoothness, r=A_r, h=A_h, center=true); // Main_rim
	translate([0,0,-A_h2/2])rotate([0,0,0])cylinder($fn=Smoothness, r=A_r2, h=A_h2, center=true); // Main_sub
}

module Asub() {
	translate([0,0,-A_h2/2+wall])rotate([0,0,0]){cylinder($fn=Smoothness, r=Asub_r, h = A_h2, center = true); } // Main	
    translate([0,0,-A_h2/2+wall]){ rotate([0,0,0]){ cylinder( $fn=Smoothness, r = Asub_r-wall, h = 100, center = true); }} // Through hole

    translate([Asub_r*sqrt(2)/2,-Asub_r*sqrt(2)/2,-A_h2/2+wall]){ rotate([0,0,0]){ cylinder( $fn=Smoothness, r = R_Accessgroove, h = A_h2, center = true); }} // Chamber access-aid hole	

    translate([-Asub_r*sqrt(2)/2,Asub_r*sqrt(2)/2,-A_h2/2+wall]){ rotate([0,0,0]){ cylinder( $fn=Smoothness, r = R_Accessgroove, h = A_h2, center = true); }} // Chamber access-aid hole	

    translate([sqrt(2)*A_r/2-2,sqrt(2)*A_r/2-2,-A_h2/2+wall]){ rotate([0,0,0]){ cylinder( $fn=Smoothness, r = Asub_r-thickwall, h = 100, center = true); }} // Cable hole

	translate([0,0,-A_LED_zpos]){ rotate([0,90,0]){ cylinder( $fn=Smoothness, r = A_LED_r, h = 100, center = true); }} // LEDs
	translate([0,0,-A_LED_zpos]){ rotate([90,0,0]){ cylinder( $fn=Smoothness, r = A_LED_r, h = 100, center = true); }} // LEDs
}

module B() {
	translate([0,0,0]){ rotate([0,0,0]){ cylinder( $fn=Smoothness, r = A_r, h = A_h, center = true); }} // Main_rim
}


module Bsub() {
	translate([0,0,-A_h2/2+wall]){ rotate([0,0,0]){ cylinder( $fn=Smoothness, r = A_r - 5, h = A_h2, center = true); }} // Main	
}

module A2() {
	translate([0,0,0]){ rotate([0,0,0]){ cylinder( $fn=Smoothness, r = A_r, h = A_h, center = true); }} // Main_rim
	translate([0,0,-A_h2/2]){ rotate([0,0,0]){ cylinder( $fn=Smoothness, r = A_r2, h = A_h2, center = true); }} // Main_sub
}

module A2sub() {
	translate([0,0,-A_h2/2+wall]){ rotate([0,0,0]){ cylinder( $fn=Smoothness, r = Asub_r, h = A_h2, center = true); }} // Main	
    translate([0,0,-A_h2/2+wall]){ rotate([0,0,0]){ cylinder( $fn=Smoothness, r = Asub_r-wall, h = 100, center = true); }} // Through hole

    translate([Asub_r*sqrt(2)/2,-Asub_r*sqrt(2)/2,-A_h2/2+wall]){ rotate([0,0,0]){ cylinder( $fn=Smoothness, r = R_Accessgroove, h = A_h2, center = true); }} // Chamber access-aid hole	

    translate([-Asub_r*sqrt(2)/2,Asub_r*sqrt(2)/2,-A_h2/2+wall]){ rotate([0,0,0]){ cylinder( $fn=Smoothness, r = R_Accessgroove, h = A_h2, center = true); }} // Chamber access-aid hole	

    translate([sqrt(2)*A_r/2-2,sqrt(2)*A_r/2-2,-A_h2/2+wall]){ rotate([0,0,0]){ cylinder( $fn=Smoothness, r = Asub_r-thickwall, h = 100, center = true); }} // Cable hole

	translate([0,0,-A_LED_zpos]){ rotate([0,90,0]){ cylinder( $fn=Smoothness, r = A_LED_r, h = 100, center = true); }} // LEDs
	translate([0,0,-A_LED_zpos]){ rotate([90,0,0]){ cylinder( $fn=Smoothness, r = A_LED_r, h = 100, center = true); }} // LEDs

    translate([0,0,-A_LED_zpos]){ rotate([45,90,0]){ cylinder( $fn=Smoothness, r = A_LED_r, h = 100, center = true); }} // LEDs NEW
	translate([0,0,-A_LED_zpos]){ rotate([-45,90,0]){ cylinder( $fn=Smoothness, r = A_LED_r, h = 100, center = true); }} // LEDs NEW

    translate([-Asub_r+5,-Asub_r+5,0]){ rotate([0,0,45]){ cube([12,Olf_width,100], center = true); }} // Olfaction stuff hole	
}

module B2() {
	translate([0,0,0]){ rotate([0,0,0]){ cylinder( $fn=Smoothness, r = A_r, h = A_h, center = true); }} // Main_rim  
}

module B2sub() {
	translate([0,0,-A_h2/2+wall]){ rotate([0,0,0]){ cylinder( $fn=Smoothness, r = A_r - 5, h = A_h2, center = true); }} // Main
}

module stage() {
    difference() {
        stage_add();
        stage_sub();
    }
}


module stage_add() {
    cube([mount_width,mount_width,stage_depth]);
    translate([-(stage_width - mount_width)/2,mount_width,0]) {
        cube([stage_width,stage_length,stage_depth]);
    };
    
}

module stage_sub() {
    
    // round stage hole
     translate([mount_width/2,mount_width + stage_length - circ_hole_rad,0]) {
        cylinder(stage_depth,circ_hole_rad,circ_hole_rad, $fn=Smoothness);
    };
    
    // space for olfactory stimulator
    translate([(mount_width - rect_hole_width)/2,rect_hole_y,0]) {
        cube([rect_hole_width,rect_hole_length,stage_depth]);
    };
    
     // center M6 screw hole
    translate([mount_width/2,mount_width/2,0]) {
        cylinder(stage_depth,screw_rad,screw_rad, $fn=Smoothness);
    };
    
     // top left M6 screw hole
    translate([screw_coord1,screw_coord2,0]) {
        cylinder(stage_depth,screw_rad,screw_rad, $fn=Smoothness);
    };
    
     // top right M6 screw hole
    translate([screw_coord2,screw_coord2,0]) {
        cylinder(stage_depth,screw_rad,screw_rad, $fn=Smoothness);
    };
    
     // bottom left M6 screw hole
    translate([screw_coord1,screw_coord1,0]) {
        cylinder(stage_depth,screw_rad,screw_rad, $fn=Smoothness);
    };
    
     // bottom right M6 screw hole
    translate([screw_coord2,screw_coord1,0]) {
        cylinder(stage_depth,screw_rad,screw_rad, $fn=Smoothness);
    };
    
 
     // magnet hole 1
    translate([magnet1_x,magnet1_y,stage_depth - magnet_depth]) {
        cylinder(magnet_depth,magnet_rad,magnet_rad, $fn=Smoothness);
    };
    
    
      // magnet hole 2
    translate([magnet2_x,magnet2_y,stage_depth - magnet_depth]) {
        cylinder(magnet_depth,magnet_rad,magnet_rad, $fn=Smoothness);
    };
    
}

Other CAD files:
Casing Files/LED-Zappelin V2 - Chrolis/DXF/Top.dxf
Casing Files/LED-Zappelin V2 - Chrolis/STL/LED-Zappelin V2 - Chrolis_Left.stl
Casing Files/LED-Zappelin V2/DXF/LED-Zappelin V2_Top.dxf
Casing Files/LED-Zappelin V2/STL/LED-Zappelin_Back.stl
Casing Files/LED-Zappelin V2 - Chrolis/LED-Zappelin V2 - Chrolis.scad
3D files/Optical Components/STL Files/1_LED_Holder.stl
3D files/Optical Components/STL Files/2_LED_Holder.stl
3D files/Optical Components/STL Files/3_LED_Holder.stl
3D files/Optical Components/STL Files/4_LED_Holder.stl
3D files/Optical Components/STL Files/5_LED_Holder.stl
3D files/Optical Components/STL Files/6_LED_Holder.stl
3D files/Optical Components/STL Files/dichroic_frame.stl
Casing Files/LED-Zappelin V2 - Chrolis/DXF/Back.dxf
Casing Files/LED-Zappelin V2 - Chrolis/DXF/Left.dxf
Casing Files/LED-Zappelin V2 - Chrolis/DXF/Right.dxf
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

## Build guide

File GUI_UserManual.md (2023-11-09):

<p align="left">

</p>

<h1 align="center"> LED Zappelin' v2.2 - GUI Instruction Manual</h1></p>

<br></br>

## Introduction
<br>

<p align="justify">
The following will detail how to control the stimulator, generate stimuli and modulate LED output.
</p>

<p align="justify">
From here we will assume that the stimulator is assembled (c.f. <a href="https://github.com/OpenSourceNeuro/LED-Zappelin-V2/blob/main/Assembly_Manual.md"> Assembly manual </a>), that drivers were installed, that an adapted power supply was selected to supply the LED driver and that all LEDs were calibrated and that their maximum intensity values were hardcoded on the microcontroller firmware (c.f. <a href="https://github.com/OpenSourceNeuro/LED-Zappelin-V2/blob/main/Installation_Manual.md"> Installation manual </a>).
</p>

<p align="justify">
The GUI (Graphical User Interface) is developed on the python libraries PyQt6/PySide6. The code is open and can be consulted and modified <a href="https://github.com/OpenSourceNeuro/LED-Zappelin-V2/tree/main/GUI">here</a>. The GUI can be run on a python virtual environment with the required libraries.
</p>

<p align="justify">
However, for convenience, an <strong>.exe</strong> file has been generated from the above code and can be found <a href="https://github.com/OpenSourceNeuro/LED-Zappelin-V2/tree"> here</a>
</p>

<br></br>

## Home page
<br>

From the main page, all software can be accessed:
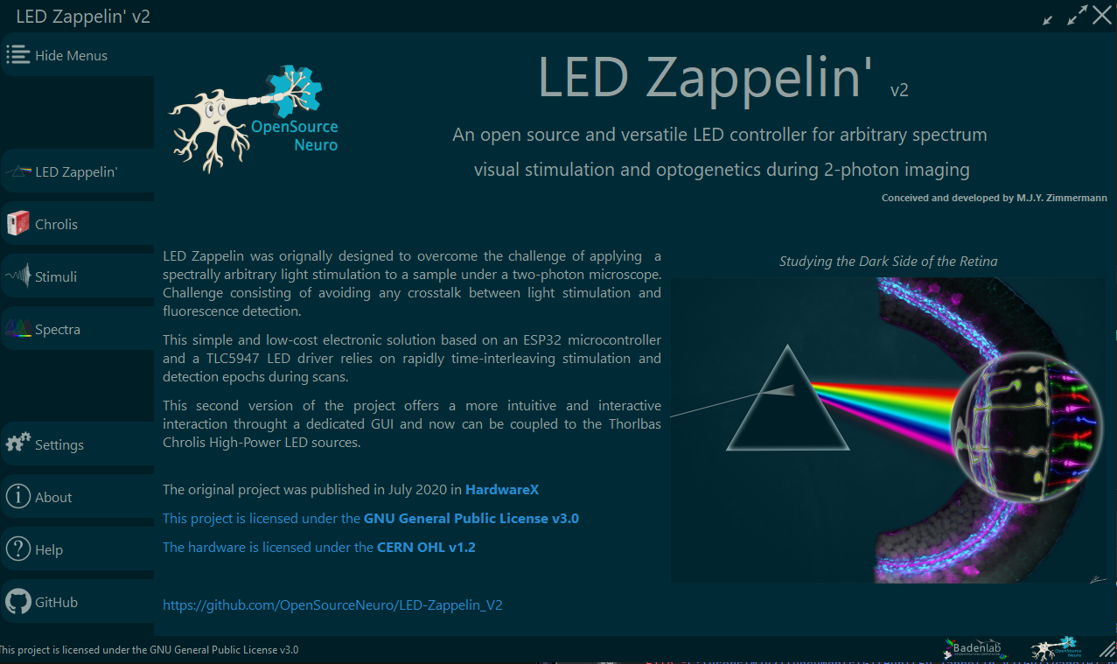
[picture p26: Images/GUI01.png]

***
- [LED Zappelin - Custom LEDs](#Custom%20LEDs)
- [LED Zappelin - Chrolis](#Chrolis)
- [Stimuli Generator](#Stimuli%20Generator)
- [Spectra](#Spectra)
***
- [Settings](#Settings)
- [About](#About)
- [Help](#Help)
- [GitHub](#GitHub)
***
<br></br>

## Custom LEDs 
<br></br>

<p align="justify">
This section of the GUI corresponds to the <strong>24 custom LEDs</strong> version of the stimulator where users can select their own stimulating LEDs. For the proxy LEDs on the front panel of the stimulator to match the order and "colours" of the stimulating LEDs, users need to update the Arduino code on the board as described in the <a href="https://github.com/OpenSourceNeuro/LED-Zappelin-V2/blob/main/Installation_Manual.md">Installation_Manual</a>.
</p>
<br>

#### Connecting the software
<br>
<p align="justify">
The GUI exchanges with the stimulator through a serial communication via a micro USB cable connected on the left side of the stimulator. First, users need to establish a serial connection with the board by selecting a <strong>COM port</strong>. If the proper COM port is selected, the proxy LEDs should light up. Next, just click on the <strong> Connect LED Zappelin'</strong> button.
</p>
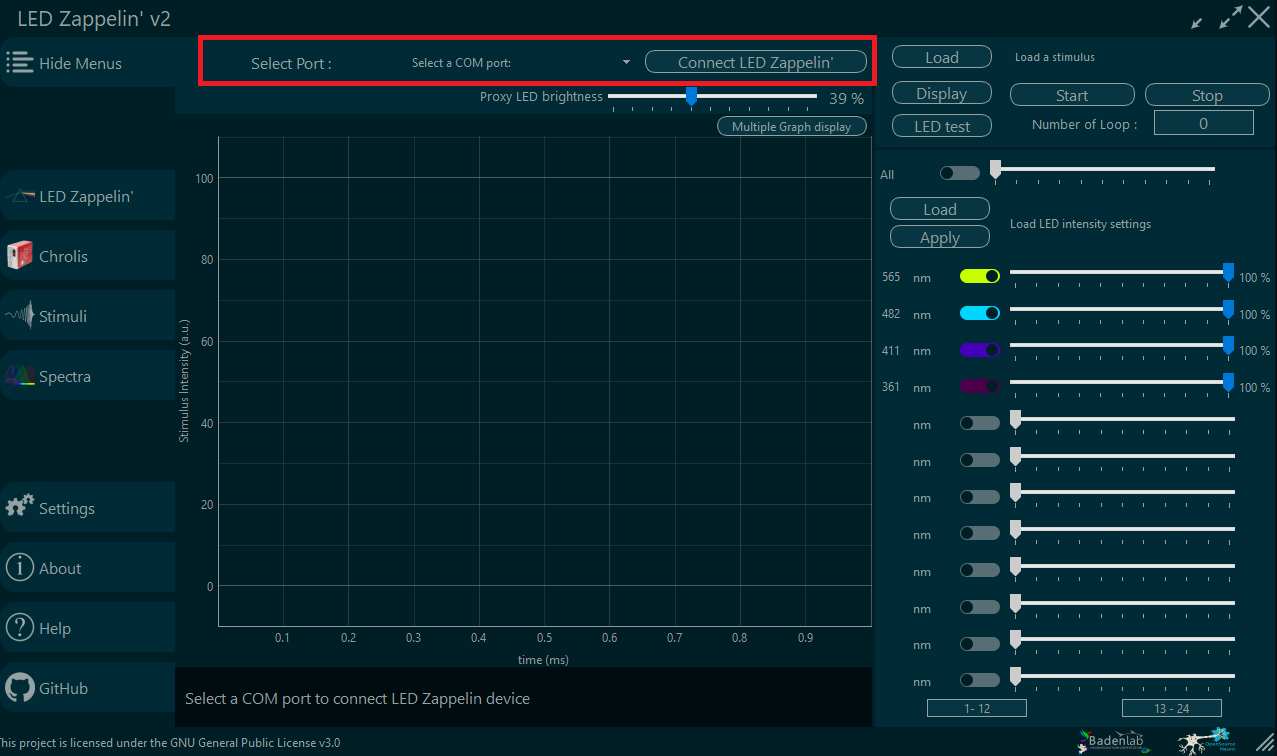
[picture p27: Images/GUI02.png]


<br>

#### Set LED
<br>

<p align="justify">
On the right-hand side of the window, users can individually control each LED maximum intensity output by adjusting the slider or manually enter a integer number on the right end of the slider, or turn if off completely by toggling the left coloured button.
</p>

<p align="justify">
This value linearly sets the new maximum intensity at which an LED would be played. A proper LED calibration (c.f. <a href="https://github.com/OpenSourceNeuro/LED-Zappelin-V2/blob/main/Installation_Manual.md"> Installation manual </a>), will ensure that the new maximum settings will accurately correspond to the slider percentage of the max calibrated value.
</p>

The top white slider above allows the user to control all LED channel at once.

<p align="justify">
For display purposes, toggle button colours correspond to the LED wavelength selected by the users and can be manually set by entering the appropriate wavelength on the left side of the slider. When a new wavelength is entered, the corresponding proxy LED will match its colour to the new wavelength value.
</p>

<p align="justify">
It is possible to select a pre-selected array of LED values and wavelength by loading a <strong>.csv</strong> file. To do so, just aove the LED sliding bars, press the <strong>Load</strong> button, select the appropriate file then click <strong>Apply</strong>.
</p>

The <strong>.csv</strong> file should be composed as follow:


The header line should not be changed

The first row corresponds to the light intensities in percentage. Only integer should be entered Here

The second row corresponds to the LED wavelength, entered here only for display purpose.

In the above example, only the first four LED channels are activated:
- LED #01 at 100% corresponding to 565nm
- LED #02 at 75% corresponding to 482nm
- LED #03 at 50% corresponding to 411nm
- LED #04 at 25% corresponding to 361nm

The <strong>.csv</strong> file should conveniently be placed in the <strong>LED_Settings</strong> folder where the <strong>.exe</strong> file is located.

<p align="justify">
Users can also check their LED status by clicking on the <strong>LED test</strong> button. This will activate the stimulating LEDs and their respective proxy LEDs according to the slider positions.
</p>

<p align="justify">
Furthermore, depending on the user light environment, the proxy LEDs might be too bright or too dim. Their brightness can then be adjusted by modulating the <strong>Proxy LED brightness</strong> slider on top of the screen. Placing this slider all the way down will just turn off the proxy LEDs. This will, obviously, only affect the proxy LEDs, not the LED ouput channels.
</p>

<br></br>

#### Loading a stimulus
<br>

Stimuli are generated as dataframes in a <strong>.csv</strong> format (c.f. [Stimuli Generator](#Stimuli%20Generator))

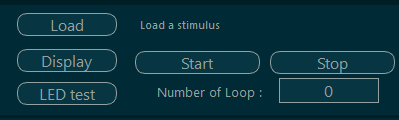
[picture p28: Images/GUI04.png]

<p align="justify">
The top right part of the screen is the stimulus panel. Here users can load, check and play the stimulus.
By clicking the <strong>Load</strong> button, users can select their pre-generated stimulation sequence, ideally from the <strong> Stimuli</strong> folder located alongside the <strong>.exe</strong> file. The stimulus file name will then be displayed on the panel for user appreciation.
</p>

In order to check the stimulation sequence, user can plot the sequence by clicking the <strong>Display</strong> button.
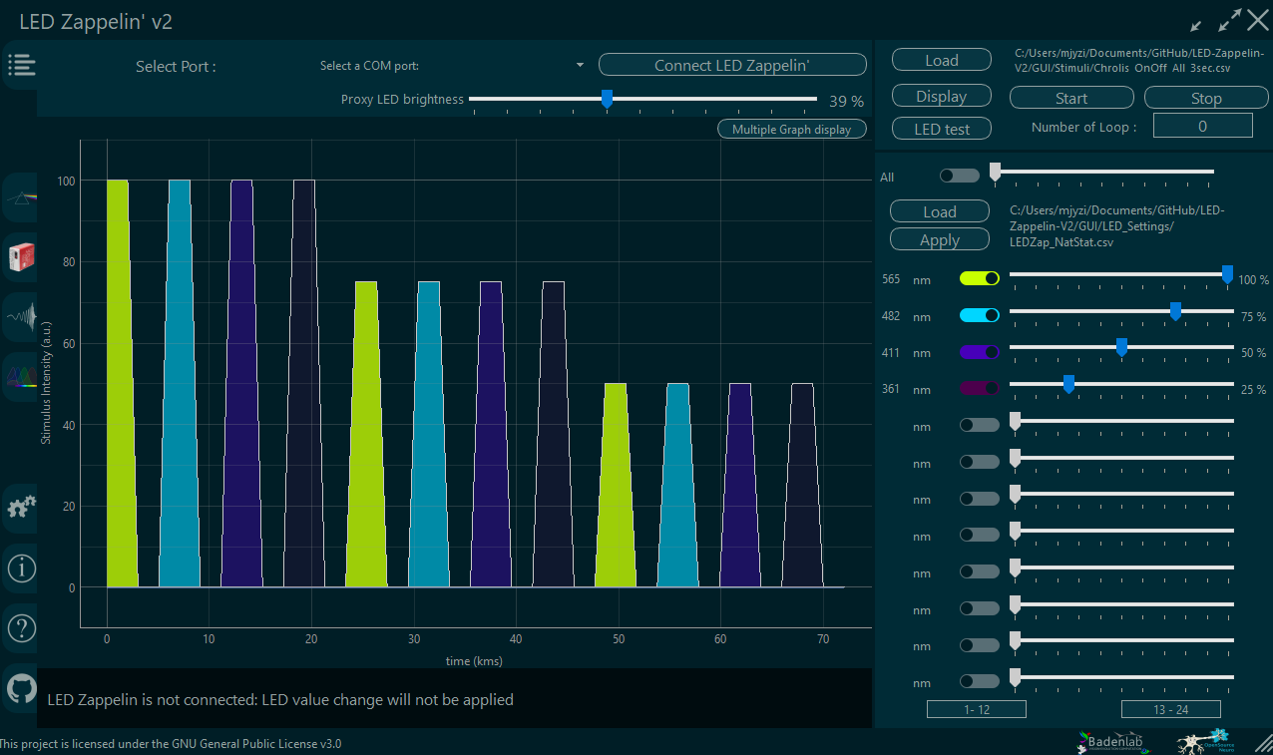
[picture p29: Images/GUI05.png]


<p align="justify">
The sequences for all activated LEDs are then displayed on the graph, their translucence corresponding to the LED intensity slider levels.
</p>

<p align="justify">
On this graph is only displayed the stimulation sequence that will be looped, the potential pre-stimulation being not displayed here (c.f. [Stimuli Generator](#Stimuli%20Generator)).
</p>

<p align="justify">
In order to check all LED sequences individually, users can click on the <strong> Multiple Graph display</strong> button above the graph.
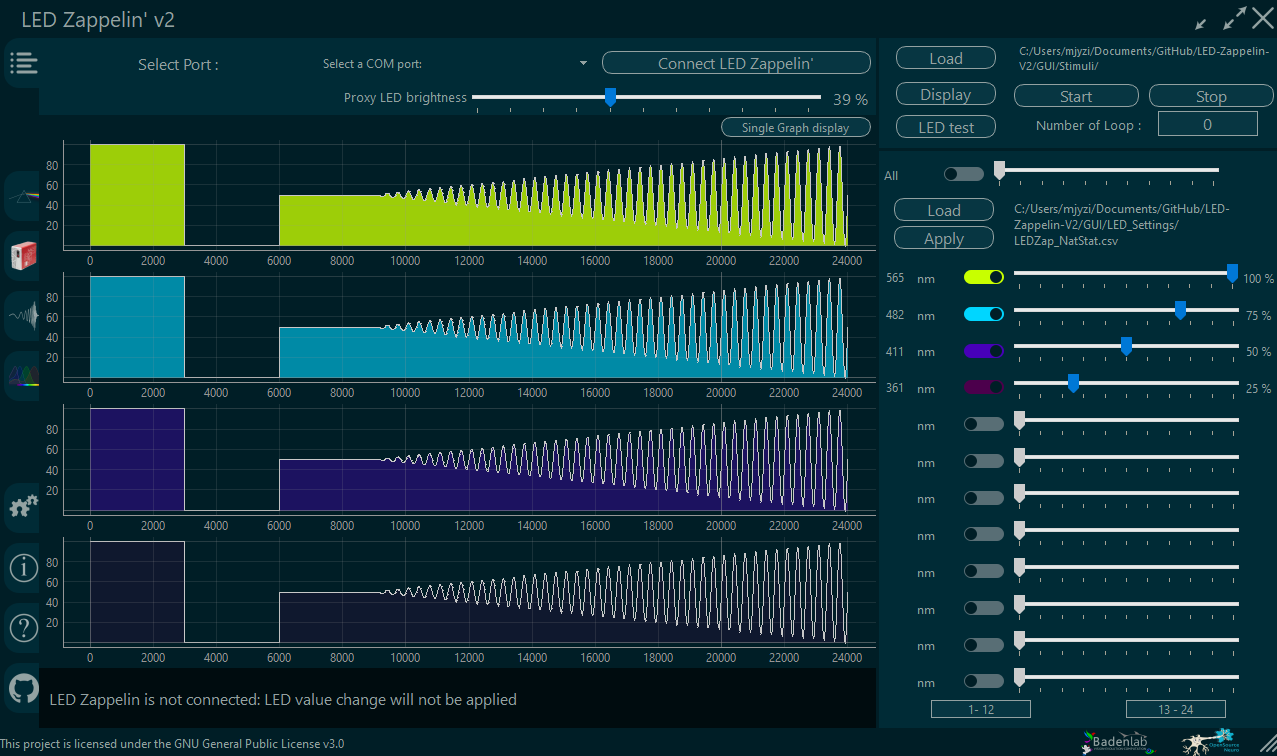
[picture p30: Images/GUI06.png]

</p>

They can also zoom in each graph, i.e. to check specific alignment in the overall sequence.

Then return to the overlapping graph by clicking on the new <strong>Single Graph display</strong> button.

<br></br>

#### Playing a stimulus
<br>

Once "loaded", a stimulus is ready to be played.

<p align="justify">
The LED sliders set the maximum intensities in percentage of the maximum calibrated value, then the stimulation sequence will operate within this range.
</p>

<p align="justify">
Users can here select the <strong>Number of Loops</strong> they need to be played. A value of 0 (by default) will see the stimulus sequence being played until the user manually stops it. Any higher integer value entered, will only play the stimulus this amount of times.
</p>

<p align="justify">
Upon clicking on the <strong>Start</strong> button, the stimulator will first play, and only once, the pre-stimulation as entered in the stimuli <strong>.csv</strong> file (c.f. [Stimuli Generator](#Stimuli%20Generator)), then play the stimulation sequence in loops. If the restimulation time is 0, then the stimulation sequence will start readily and the monitor at the bottom of the screen will displayed the current loop number being played.
</p>

<p align="justify">
When clicked, the <strong>Start</strong> button will light up in red.
Clicking the <strong>Stop</strong> button will stop the stimulation sequence and return the stimulation settings to its ready conditions.
</p>

<br></br>

***
<br>

## Chrolis 
<br></br>

Mostly identical to the 24 custom LED

<strong>To Be Completed</strong>

<br></br>
***

## Stimuli Generator 
<br></br>

<p align="justify">
A stimuli generator tab can be found on the GUI and allows users to generate simple stimuli on the fly.
</p>

<p align="justify">
However, we recommend users to generate their own stimuli using whatever programming language they prefer.
</p>

<p align="justify">
Here we provided <a href="https://github.com/OpenSourceNeuro/LED-Zappelin-V2/tree/main/Notebooks">python jupyter notebook</a> with visualisation graph to generate the most common stimuli in our field. These notebooks can be easily modify to generate any sequence users might need.
</p>

<p align="justify">
The only thing that matters, no matter the programming language chosen, is to export the stimulation sequence as a <strong>.csv</strong> dataframe, just as follow:
</p>

<br>

LED values are expressed in percentage, and the time values are expressed in micro-seconds.

The header line labels need to be respected in order to be read properly by the software.

<p align="justify">
Let's only consider the 12 first columns (columns A to L) (or less or more depending on your stimulator version): these columns corresponds to the sequential values (in percentage of the max set intensities) that will be output for each LED channels.

<p align="justify">
The first row (line 2) only concerns the pre-stimulation (pre-adaptation) period that is only going to be played once, at the very start of the stimulation and for a period of time indicate in the first row of the <strong>Pre-Adaptation</strong> column (P2) in microseconds. A value of 0 will simply skip the pre-adaptation. The other row values will be ignored
</p>

<p align="justify">
The sequence then starts on the second row (row 3) and will/could be looped back to this point when the sequence is over.
</p>

<p align="justify">
The first row of the <strong> Resolution</strong> column (M2) indicates the amount of time each row value will be played in microseconds. The other row values will be ignored.
</p>

<p align="justify">
For the GUI to keep track of the stimulation sequence, the number of value entries (without the pre-adaptation) needs to be entered on the first row of <strong> nEntries</strong> (N2). The other row values will be ignored.
</p>

<p align="justify">
The <strong>Trigger</strong> column sets the trigger output from the stimulator in the form of a 3.3V pulse with a duration by default of 100 000 microseconds which can be modified on the Arduino code>General_Settings.h>TriggerDuration (Do not forget to reupload the code on the board afterwards).
</p>

The first row (O2) sets the trigger mode:

- A <strong>"n = 0"</strong>  value will only play a trigger once, when the stimulation starts (and after an eventual pre-adaptation).

- A value of <strong>"n = 1"</strong>  will play a Trigger in a repeated fashion, starting at the beginning of the stimulation sequence (and after an eventual pre-adaptation), and will occur every x microseconds. x being the value entered in the row below (O3). It is encouraged in this mode to generate stimuli that will end at a multiple of x in order to properly align the stimulation and recording session during the data pre-analysis.

- A value <strong>"n = >1"</strong> will output n different triggers with inter-trigger length equal to the value O(2+i) (for i within n). In this mode, it is encouraged that the sum of all inter-trigger length matches the length of the entire stimulation sequence, once again for alignment purposes.

<br>

Overall, the stimulus presented above can be read as follow:
- The sequence is made of 72 points, each lasting 1 seconds (1 000 000 microseconds)
- A pre-adaptation of 3 seconds (3 000 000 microseconds) will be played only once at the begining of the stimulation with all 12 LEDs on at 25% of their max set intensities (set calibration eventually linearly tuned down by LED sliders).
- During the stimulation, a trigger will be produced every second (1 000 000 microseconds).
- The beginning of the stimulation apparently consists of a sequential activation(on/off) in order of the first 5 LEDS (for 1 sec (resolution value))
<br></br>
***

## Spectra 
<br></br>
<strong>To Be Completed</strong>
<br></br>
***

## Settings 
<br></br>
<strong>To Be Completed</strong>
<br></br>
***

## About 
<br></br>
<strong>To Be Completed</strong>
<br></br>
***

## Help 
<br></br>
<strong>To Be Completed</strong>
<br></br>
***

## GitHub 
<br></br>
<strong>To Be Completed</strong>
<br></br>
***

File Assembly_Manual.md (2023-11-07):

<p align="left">

</p>

<h1 align="center"> LED Zappelin' v2.2 - Assembly Manual</h1></p>

<br></br>

## Overview

<p align="justify">
This page contains detailed assembly instructions for both version of LEDF Zappelin', and includes a parts list for purchasing all electronics components.
Instructions on how to upload and update the microcontroller code and how to calibrate the device can be found <a href="https://github.com/OpenSourceNeuro/LED-Zappelin-V2/blob/main/Installation_Manual.md"> <strong>here</strong> </a>.
Instructions regarding the GUI and on how to design stimuli can be found <a href="https://github.com/OpenSourceNeuro/LED-Zappelin-V2/blob/main/GUI_UserManual.md"><strong>here</strong></a>
</p>

***

- [Ordering PCB](#Ordering-the-PCB)
- [Assembling LED Zappelin' - LED version](#Assembling-the-LED-version)
- [Assembling LED Zappelin' - Chrolis version](#Programming-the-ESP32)

***

## Ordering the PCB

<p align="justify">
First step consist in getting the stimulator board.
The PCB source files were designed on <a href="http://kicad.org/">KiCAD 6.0</a> and are available to be modified by users if need be.
They can be found on the GitHub repository <a href="https://github.com/OpenSourceNeuro/LED-Zappelin-V2/tree/main/PCB">PCB section</a>, where one can find the "Gerber" files that companies (i.e. <a href="https://jlcpcb.com">JLCPCB</a>) will request to manufacture PCBs.
</p>

<p align="justify">
For the LED version two boards are required, the <a href="https://github.com/OpenSourceNeuro/LED-Zappelin-V2/tree/main/PCB/LED-Zappelin-V2">main board</a> and the <a href="https://github.com/OpenSourceNeuro/LED-Zappelin-V2/tree/main/PCB/LED-Zappelin-V2-ResistorBoard">resistors board</a>.
</p>

<p align="center">
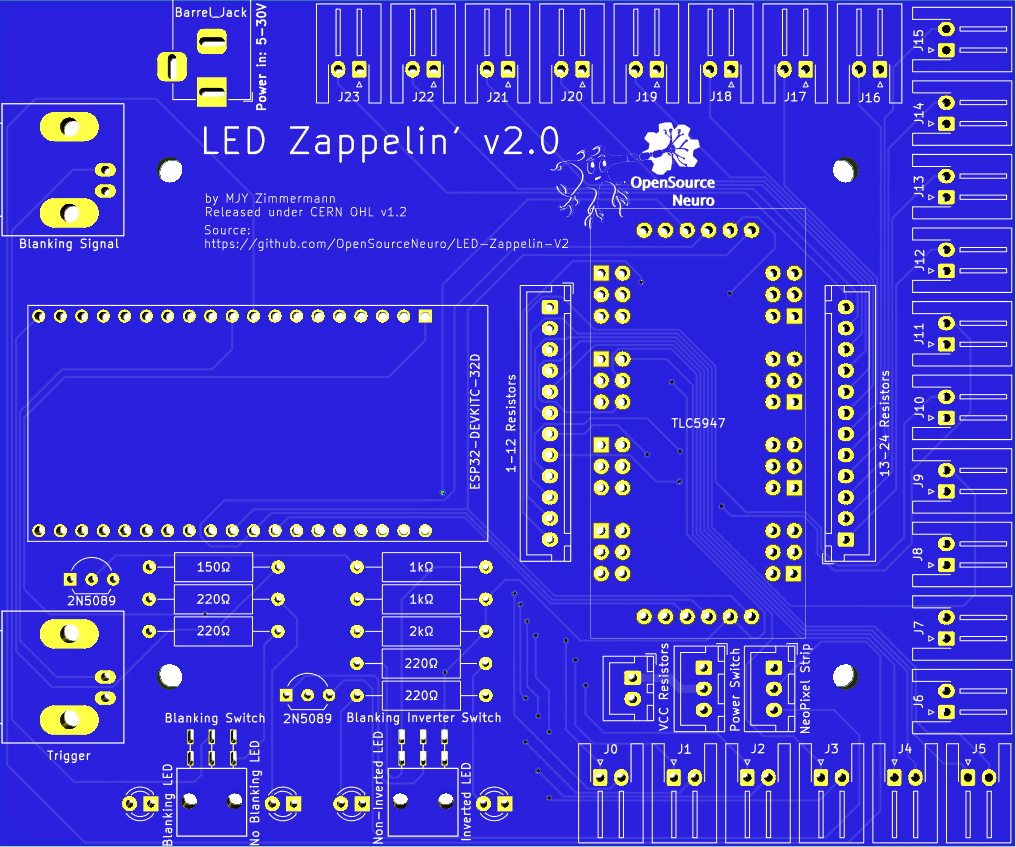
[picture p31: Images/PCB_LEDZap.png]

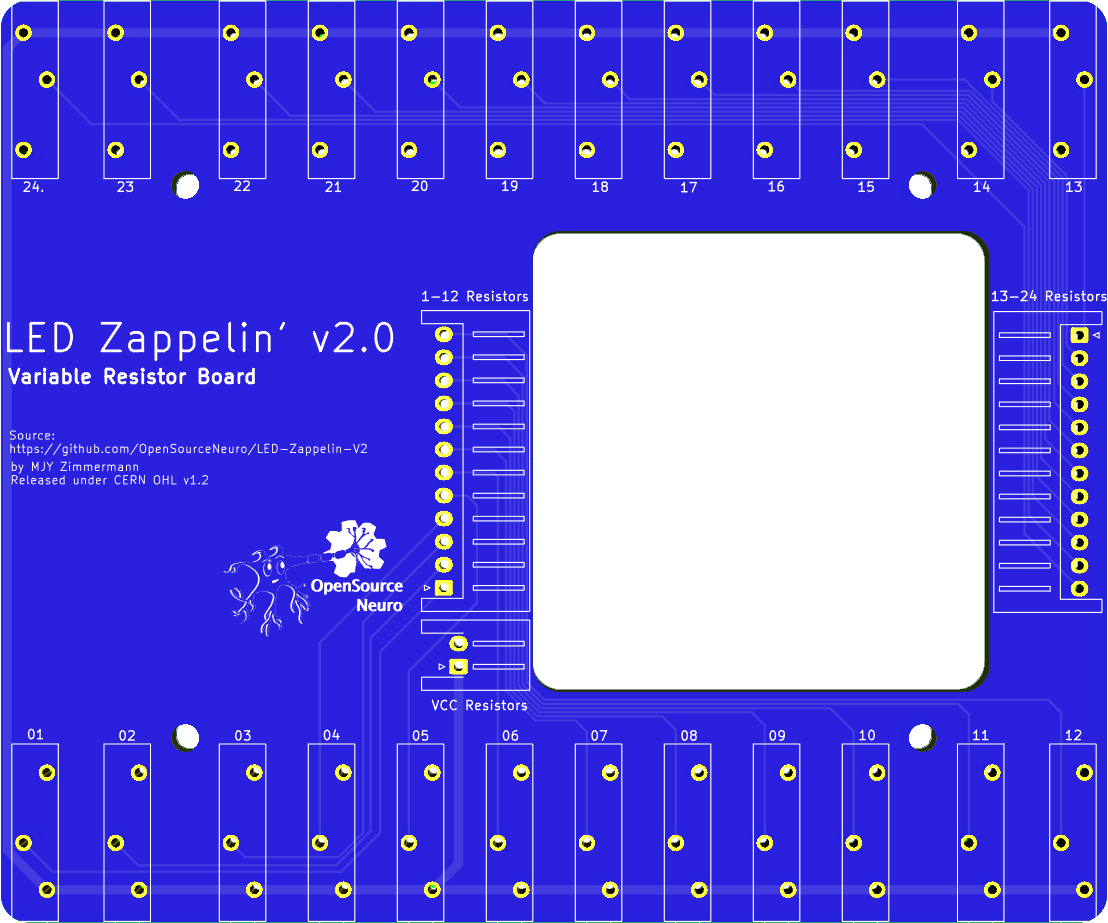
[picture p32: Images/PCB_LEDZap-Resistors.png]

</p>

For the Chrolis version, only the <a href="https://github.com/OpenSourceNeuro/LED-Zappelin-V2/tree/main/PCB/LED-Zappelin-V2-Chrolis"> main board</a> is required

<p align="center">
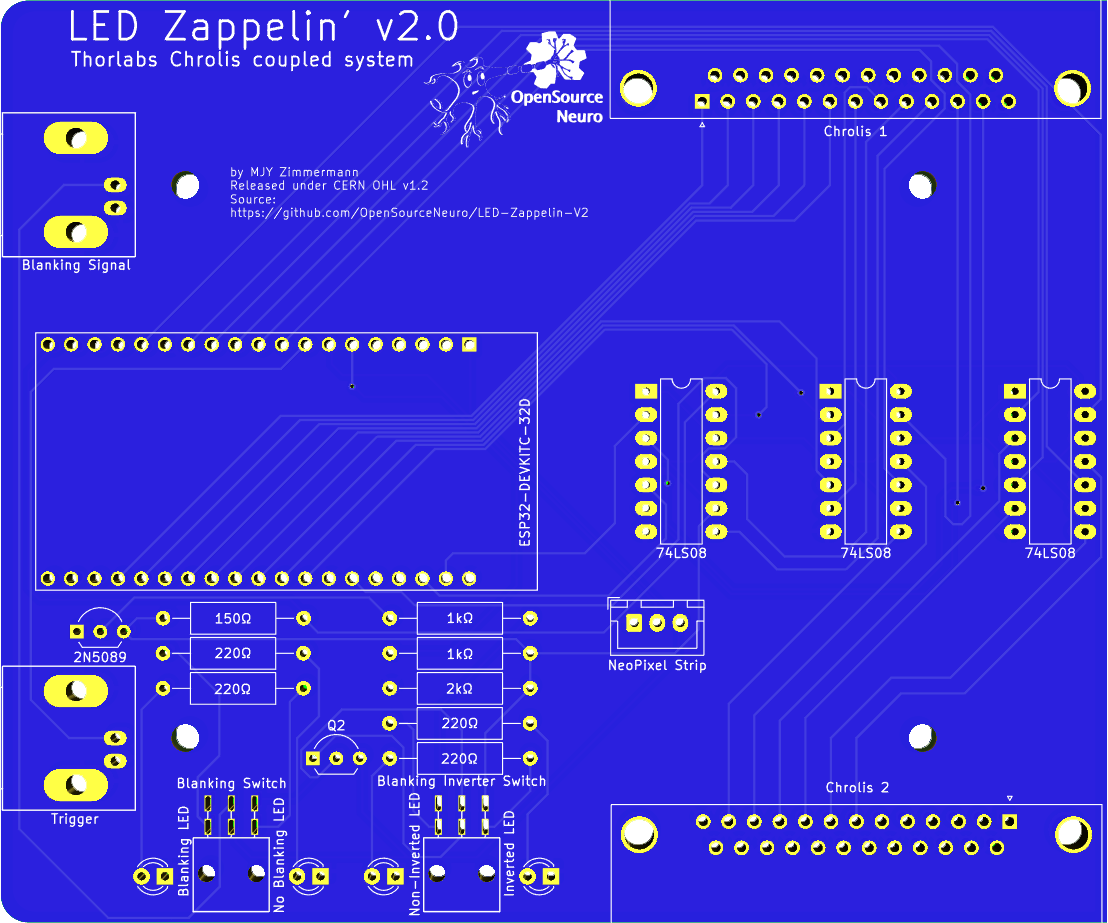
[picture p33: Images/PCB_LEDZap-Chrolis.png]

</p>

<br>
</br>

## Assembling the LED version

Components can be sources from the <a href="">BoM</a> or <a href="">KitSpace</a>

<p align="justify">
The board itself is self-explanatory. There is no need to solder more JST pins nor trimmer resistors than the number of LED required for the desired stimulator.
</p>

<p align="justify">
The first switch on the left allows the user to enable the blanking function. When enabled, LED channels output will be blanked while receiving a "blanking" signal. The second switch allow the user to invert such blanking signal. For example, ScanImage users, will require such inversion.
</p>

</br>

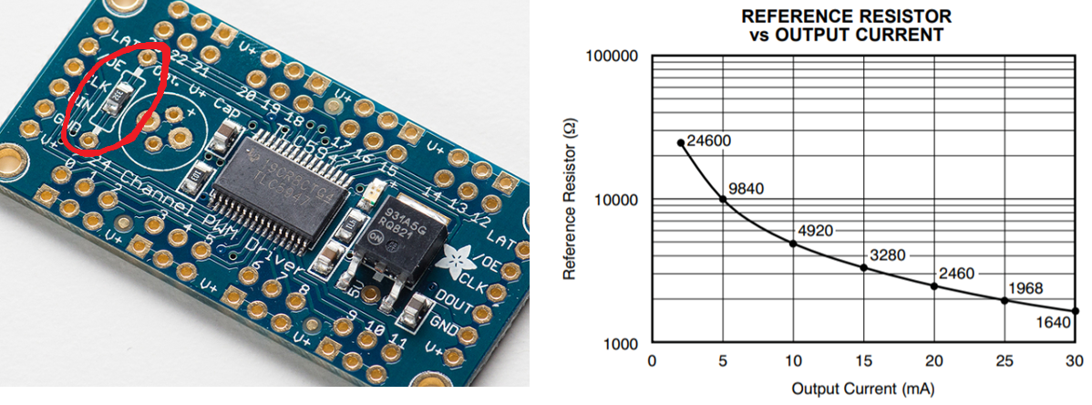
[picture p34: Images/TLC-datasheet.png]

<p align="justify">
The Adafruit TLC5947 LED driver is a constant current driver configured by default to set the current level at 15mA per channel, which is virtually safe for any LED. However, one can operate at different current by replacing the on-board reference resistor with a through hole resistor. The driver is capable to deliver up to 30mA, the graph shows the relationship between resistance and output current.
</p>

<br></br>

<p align="justify">
The stimulator casing can either be 3D printed (<a href="https://github.com/OpenSourceNeuro/LED-Zappelin-V2/tree/main/Casing%20Files/LED-Zappelin%20V2/STL">STL Files</a>) or laser cut (<a href="https://github.com/OpenSourceNeuro/LED-Zappelin-V2/tree/main/Casing%20Files/LED-Zappelin%20V2/DXF">DXF Files</a>)
</p>

<p align="center">
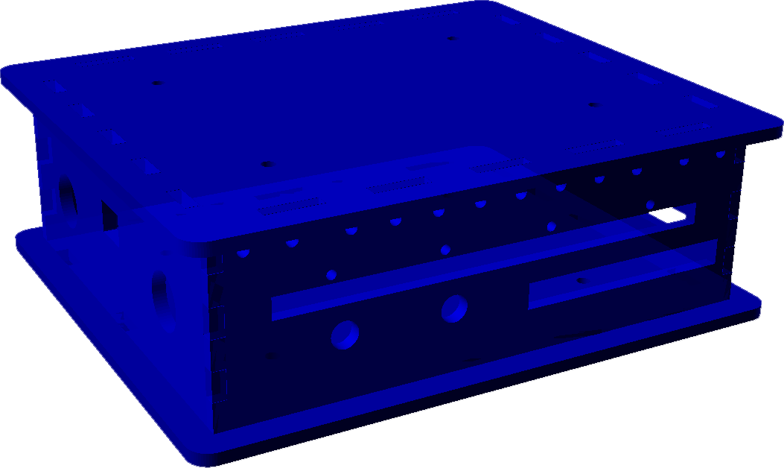
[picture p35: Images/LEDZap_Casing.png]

</p>

<p align="justify">
The default casing is designed to hold a 2*8 neopixel stick that can be used as LED proxy for the user to check the ongoing status of the stimulation in the system.
</p>

<p align="center">
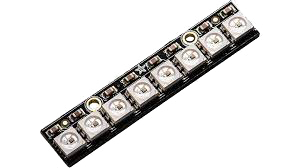
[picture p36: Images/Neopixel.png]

</p>

<br>
</br>

## Assembling the Chrolis version

Components can be sources from the <a href="">BoM</a> or <a href="">KitSpace</a>

<p align="justify">
The assemly of this board is very similar to the previous one. the TLC LED driver is here replaced by a series of TTL logic AND gates which output to two D-SUB25 port to be connected with two chrolis systems.
</p>

The stimulator casing can either be 3D printed (<a href="https://github.com/OpenSourceNeuro/LED-Zappelin-V2/tree/main/Casing%20Files/LED-Zappelin%20V2%20-%20Chrolis/STL">STL Files</a>) or laser cut (<a href="https://github.com/OpenSourceNeuro/LED-Zappelin-V2/tree/main/Casing%20Files/LED-Zappelin%20V2%20-%20Chrolis/DXF">DXF Files</a>)

<p align="center">
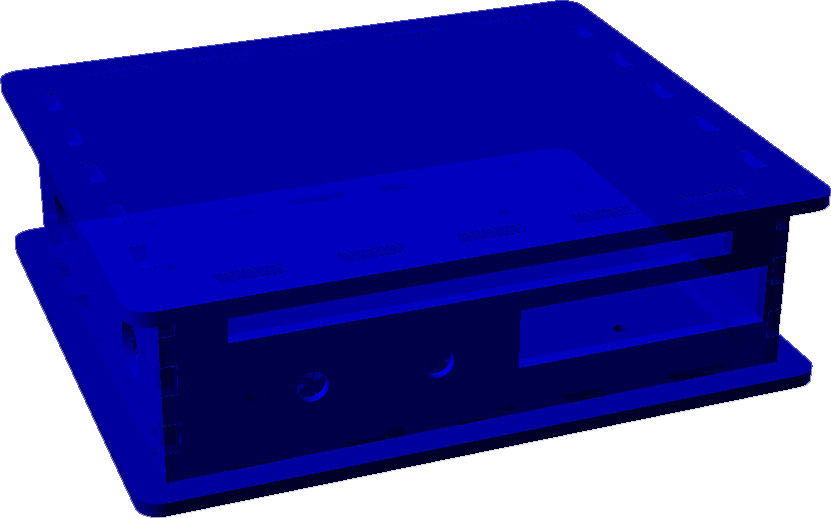
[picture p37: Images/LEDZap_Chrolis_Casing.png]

</p>

The default casing is designed to hold a 2*8 neopixel stick that can be used as LED proxy for the user to check the ongoing status of the stimulation in the system.

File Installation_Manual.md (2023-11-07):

<p align="left">

</p>

<h1 align="center"> LED Zappelin' v2.2 - Installation Manual</h1></p>

<br></br>

## Hardware
<br>

<p align="justify">
On the stimulator board, LEDs are controlled by the <a href="https://www.adafruit.com/product/1429">  TLC5947</a> LED driver. This is a constant current driver, which is exactly what it is required for precise LED intensity control.
</p>

<p align="justify">
A constant current driver gives some flexibility with the supply voltage and dismiss the need to use current limiting resistors. Stimulating LEDs can then be connected directly to the LED output on the device.
</p>

<p align="justify">
The TLC5947 driver will adjust automatically to any power supply fluctuation, preventing LED to flicker, increasing their life-spam and maintaining their efficiency over time, hence reducing maintenance calibration or replacement.
</p>

<p align="justify">
The board on the stimulator is set by default to deliver 15mA per LED channel, which is safe to virtually all LEDs that can be purchased on the market. However it is possible to operate the LED channels at different currents by replacing the on-board reference resistor with a through-hole resistor. The maximum current level at which the TLC5947 driver can operate being 30mA per channel
</p>


<p align="justify">
The location of the through-hole resistor is circled in red and the following graph shows the relationship between the resistance and the driver output current. If the user wants / needs to change the current output, the LED datasheet will provide the optimal forward current required. Still it is not expected that such current change would be necessary.
</p>

<p align="justify">
The TLC driver is powered separately from the microcontroller, from the back of the device and can take 5v to 30V. Since the TLC is a constant current driver, the voltage selection is not really critical. It just needs to be slightly higher than the LEDs forward voltage (typically around 3v for standard LEDs). In doubt consult the LED datasheet
</p>

<br></br>

## Driver Installation
<br>

LED Zappelin runs on an Espressif ESP32 board and requires the USB to UART bridge <a href="https://www.silabs.com/developers/usb-to-uart-bridge-vcp-drivers"> CP210x driver</a>,  which can be downloaded<a href="https://www.silabs.com/developers/usb-to-uart-bridge-vcp-drivers?tab=downloads"> <strong>here</strong></a>.

Once the driver has been installed, users can operated the GUI (c.f. <a href="https://github.com/OpenSourceNeuro/LED-Zappelin-V2/blob/main/GUI_UserManual.md"> GUI UserManual</a>) or modify the <a href="https://github.com/OpenSourceNeuro/LED-Zappelin-V2/tree/main/Arduino">microcontroller code</a> through the Arduino Integrated Development Environment (IDE).

<br></br>

## Microcontroller Arduino code

<br>

##### Arduino IDE

<br>

The ESP32 microcontroller runs a C++ code which can be accessed via the Arduino IDE, which can be downloaded <a href="https://www.arduino.cc/en/software">here</a>.

<br>

##### ESP32 Add-on

<br>

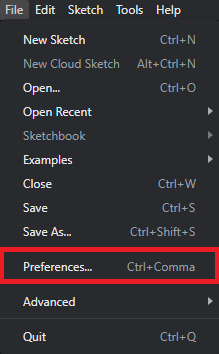
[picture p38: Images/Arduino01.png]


Once the IDE is installed, users needs to install the ESP32 board library:

In the Arduino IDE, go to <strong> File > Preferences </strong>

Enter the following link into the <strong>Additional Board Manager URLs</strong> field:

https://raw.githubusercontent.com/espressif/arduino-esp32/gh-pages/package_esp32_index.json

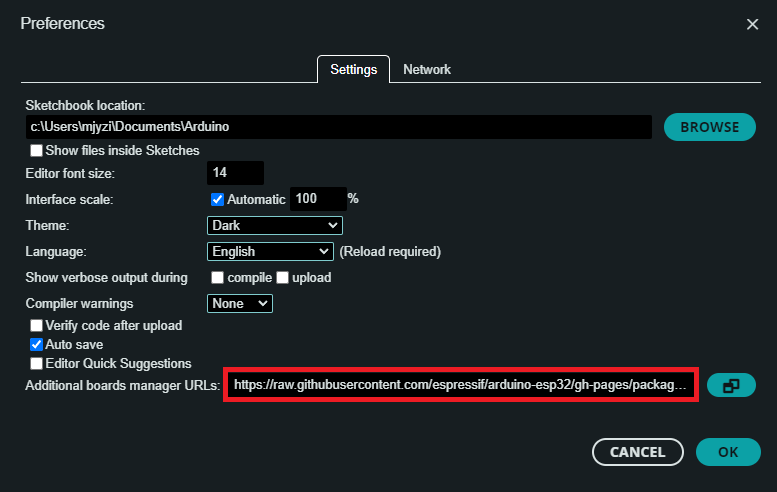
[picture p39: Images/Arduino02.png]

Then click on the <strong>OK</strong> button.

<br></br>

Next, open the Boards Manager. Go to <strong> Tools > Board > Board Manager...</strong>

Search for ESP32 and press install button for the <strong>ESP32 by Espressif Systems</strong>.

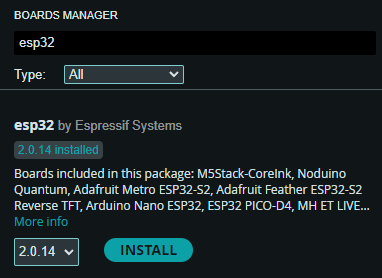
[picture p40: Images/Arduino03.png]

Then click on the <strong>Install</strong> button.

<br></br>

##### Compiling the code

<br>

Within the Arduino IDE, user needs to select the FQBN (Fully Qualified Board Name) on which the code will be compiled for.

Here the ESP32 Dev Module needs to be selected.

Go to <strong>Tools > Board > esp32 > ESP32 Dev Module </strong>


The board name should be displayed  as shown.

<br></br>

Before compiling the LED Zappelin code, a few librairies need to be installed:
  - Arduino-SerialCommand
  - Adafruit_TLC5947
  - Adafruit_NeoPixel

Most of them can be downloaded from the Arduino IDE: Go to <strong>Sketch > Include Librairy > Manage Libraries</strong>, enter the library name, then install it following the same process as for the board library.

We however recommend for the Arduino-SerialCommand library to manually place the library folder which can be found <a href="https://github.com/OpenSourceNeuro/LED-Zappelin-V2/tree/main/Arduino/Librairies">here</a> into the library folder. For Windows Users: <strong>C:/Users/x/Documents/Arduino/libraries</strong>

Now everything is set to compile and verify the code.

Users can now select the COM port on which the ESP32 is connected ( Go to <strong>Tools > port</strong> ) and upload the code onto the board.

<br></br>

##### Code and calibration

<br>

The code runs continuously on the board in a loop detailed in the main tab (LED_Zappelin_V2.ino).
To not interfere with the proper function and communication of the program, avoid modifying this part of the code.

<br>

In <strong>General_Settings.h</strong>:

- There exists two versions for the NeoPixel strips that serve as proxy LEDs for the device. If the proxy LEDs do not display the appropriate colours, comment/uncomment the Adafruit_NeoPixel functions:


<br>

In <strong> LED_Values.h </strong>

- Users can select here the colours displayed by the proxy LEDs by entering the wavelength corresponding to each stimulating LEDs.
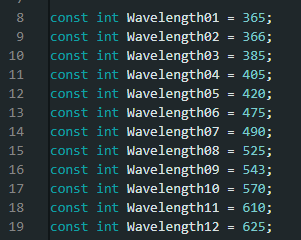
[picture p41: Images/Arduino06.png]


- The TLC5947 is a linear current-sink LED driver with a 12bits resolution (4096 values).
However, some LEDs may reach their maximum intensities before reaching the maximum stimulating value (4095). A calibration step is then require here.

    Trimmer potentiometers corresponding to each LED channels can be found on the device. They regulate the maximum current intensity each stimulating LED can be drove with.

    First, user need to set each stimulating LED to their desired maximum intensity by adjusting the potentiometer value.

    Once done, play a <a href="">step-increased stimulation sequence</a> for the tested LED and not at which value the LED maximum intensity is reached and (may?) plateau.

    Finally enter the noted value in the <strong> LED_Values.h</strong> tab.
    

    <br></br>

    Reupload the code onto the board, now the tested LED will have a linear intensity increase from 0 to 100% without any saturation.

<br></br>

No further modification of the code is then required from the user who can now control the board directly from the GUI.

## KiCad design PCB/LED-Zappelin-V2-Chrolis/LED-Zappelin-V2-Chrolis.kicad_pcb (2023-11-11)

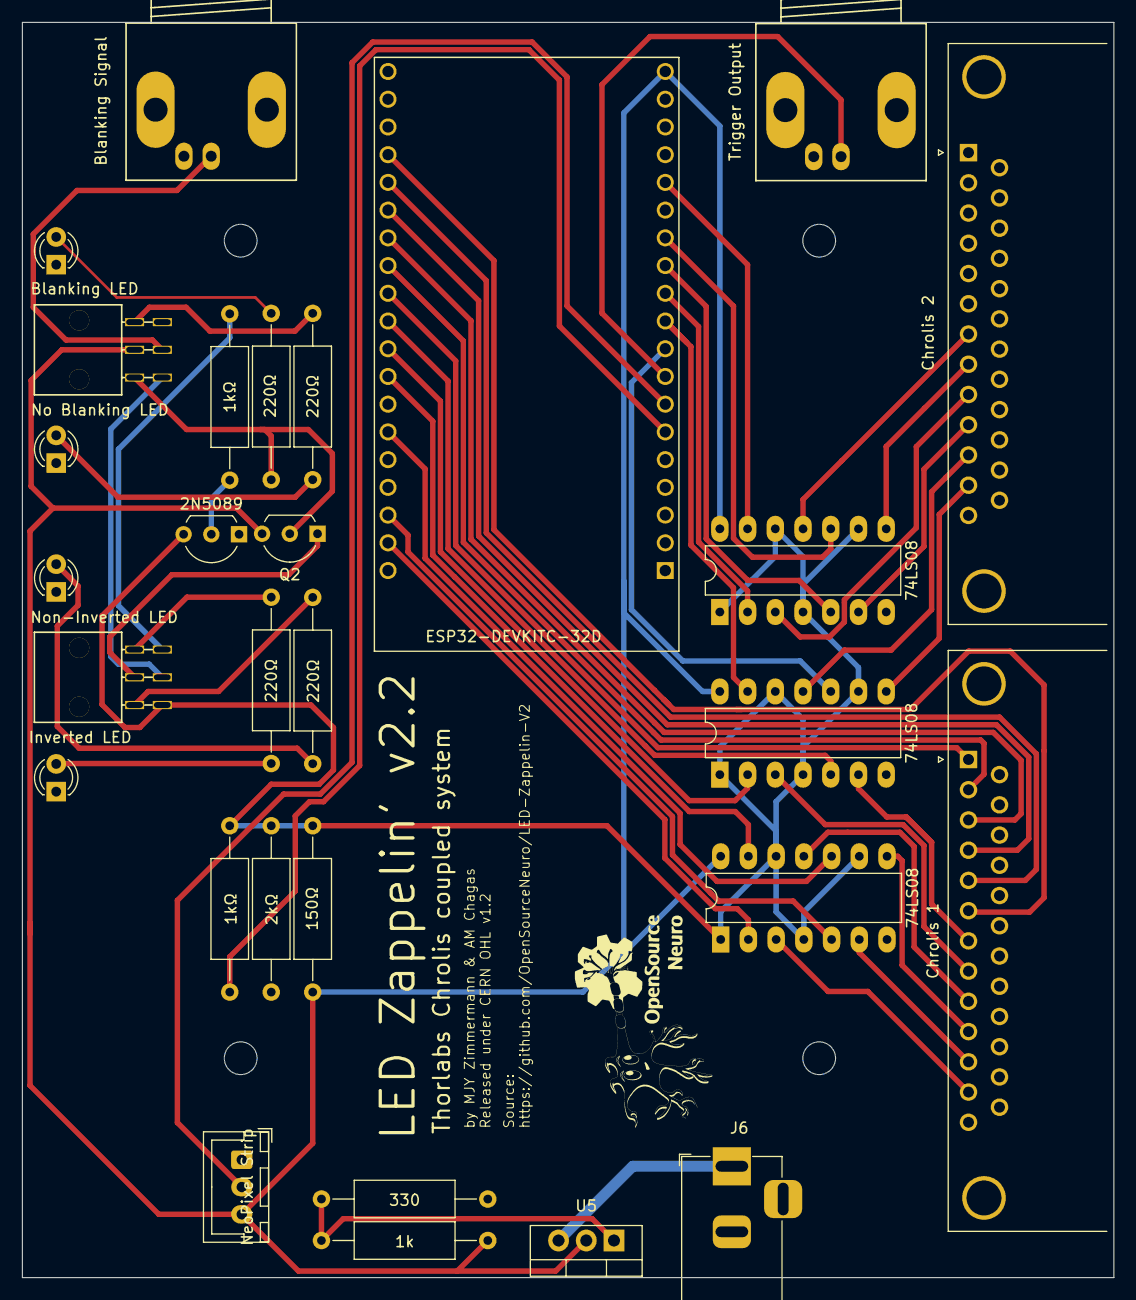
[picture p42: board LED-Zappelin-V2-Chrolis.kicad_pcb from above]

Board: 2 copper layers, 100.0 x 115.0 mm, 33 parts (0 on the bottom side), 51 nets.

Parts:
D1: Blanking LED; LED_D3.0mm
D2: No Blanking LED; LED_D3.0mm
D3: Inverted LED; LED_D3.0mm
D4: Non-Inverted LED; LED_D3.0mm
H1, H2, H3, H4: MountingHole; MountingHole_3mm
J1: Blanking Signal; BNC_Socket_TYCO-AMP_LargePads
J2: Trigger Output; BNC_Socket_TYCO-AMP_LargePads
J3: Chrolis 1; DSUB-25_Female_Horizontal_P2.77x2.84mm_EdgePinOffset9.90mm_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
J4: Chrolis 2; DSUB-25_Female_Horizontal_P2.77x2.84mm_EdgePinOffset9.90mm_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
J5: NeoPixel Strip; JST_XH_B3B-XH-A_1x03_P2.50mm_Vertical
J6: Barrel_Jack; BarrelJack_Horizontal
Q1, Q2: 2N5089; TO-92L_Inline_Wide
R1, R6: 1kΩ; R_Axial_DIN0309_L9.0mm_D3.2mm_P15.24mm_Horizontal
R2: 2kΩ; R_Axial_DIN0309_L9.0mm_D3.2mm_P15.24mm_Horizontal
R3, R4, R7, R8: 220Ω; R_Axial_DIN0309_L9.0mm_D3.2mm_P15.24mm_Horizontal
R5: 150Ω; R_Axial_DIN0309_L9.0mm_D3.2mm_P15.24mm_Horizontal
R9: 1k; R_Axial_DIN0309_L9.0mm_D3.2mm_P15.24mm_Horizontal
R10: 330; R_Axial_DIN0309_L9.0mm_D3.2mm_P15.24mm_Horizontal
SW1: Blanking Switch; maxi_DPDT_Angled
SW2: Blanking Inverter Switch; maxi_DPDT_Angled
U1: ESP32-DEVKITC-32D; MODULE_ESP32-DEVKITC-32D
U2, U3, U4: 74LS08; DIP-14_W7.62mm_LongPads
U5: LM317_TO-220; TO-220-3_Vertical

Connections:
5V: J5.3, Q2.3 (C), R5.2, R9.2, SW1.5 (B), U1.19 (EXT_5V), U2.14 (VCC), U3.14 (VCC), U4.14 (VCC), U5.2 (VO)
+9V: J6.1, U5.3 (VI)
Blanking: Q1.3 (C), R1.2, R2.2, R5.1, SW2.3 (C), U2.1, U2.4, U2.9, U2.12, U3.1, U3.4, U3.9, U3.12, U4.1, U4.4, U4.9, U4.12
GNDREF: D1.1 (K), D2.1 (K), D3.1 (K), D4.1 (K), J1.2 (Ext), J2.2 (Ext), J3.13, J3.14, J3.15, J3.16, J3.17, J3.18, J3.19, J3.20, J3.21, J3.22, J3.23, J3.24, J3.25, J4.13, J4.14, J4.15, J4.16, J4.17, J4.18, J4.19, J4.20, J4.21, J4.22, J4.23, J4.24, J4.25, J5.1, J6.2, Q1.1 (E), R2.1, R10.1, U1.14 (GND1), U1.20 (GND3), U1.26 (GND2), U2.7 (GND), U3.7 (GND), U4.7 (GND)
GPIO00: J3.4, U1.33 (IO0)
GPIO02: J3.5, U1.34 (IO2)
GPIO04: J3.3, U1.32 (IO4)
GPIO05: U1.29 (IO5), U3.5
GPIO12: U1.13 (IO12), U4.10
GPIO13: U1.15 (IO13), U4.13
GPIO15: J3.6, U1.35 (IO15)
GPIO16: J3.2, U1.31 (IO16)
GPIO17: J3.1, U1.30 (IO17)
GPIO18: U1.28 (IO18), U3.2
GPIO19: U1.27 (IO19), U2.13
GPIO21: U1.25 (IO21), U2.10
GPIO22: U1.22 (IO22), U2.5
GPIO23: U1.21 (IO23), U2.2
GPIO25: U1.9 (IO25), U3.10
GPIO26: U1.10 (IO26), U3.13
GPIO27: U1.11 (IO27), U4.2
GPIO28: U1.12 (IO14), U4.5
GPIO Input 1: J3.12, U2.3
GPIO Input 2: J3.11, U2.6
GPIO Input 3: J3.10, U2.8
GPIO Input 4: J3.9, U2.11
GPIO Input 5: J3.8, U3.3
GPIO Input 6: J3.7, U3.6
GPIO Input 7: J4.12, U3.8
GPIO Input 8: J4.11, U3.11
GPIO Input 9: J4.10, U4.6
GPIO Input 10: J4.9, U4.3
GPIO Input 11: J4.8, U4.8
GPIO Input 12: J4.7, U4.11
NeoPixel: J5.2, U1.7 (IO32)
unnamed: D1.2 (A), R3.1
unnamed: D2.2 (A), R4.1
unnamed: D3.2 (A), R7.1
unnamed: D4.2 (A), R8.1
unnamed: J1.1 (In), SW1.2 (B)
unnamed: Q1.2 (B), R6.1
unnamed: Q2.2 (B), R3.2, SW1.6 (C)
unnamed: Q2.1 (E), SW2.5 (B)
unnamed: R4.2, SW1.4 (A)
unnamed: R6.2, SW2.1 (A)
unnamed: R7.2, SW2.4 (A)
unnamed: R8.2, SW2.6 (C)
unnamed: SW1.3 (C), SW2.2 (B)
unnamed: R1.1, U1.6 (IO35)
unnamed: R9.1, R10.2, U5.1 (ADJ)
Trigger: J2.1 (In), U1.8 (IO33)

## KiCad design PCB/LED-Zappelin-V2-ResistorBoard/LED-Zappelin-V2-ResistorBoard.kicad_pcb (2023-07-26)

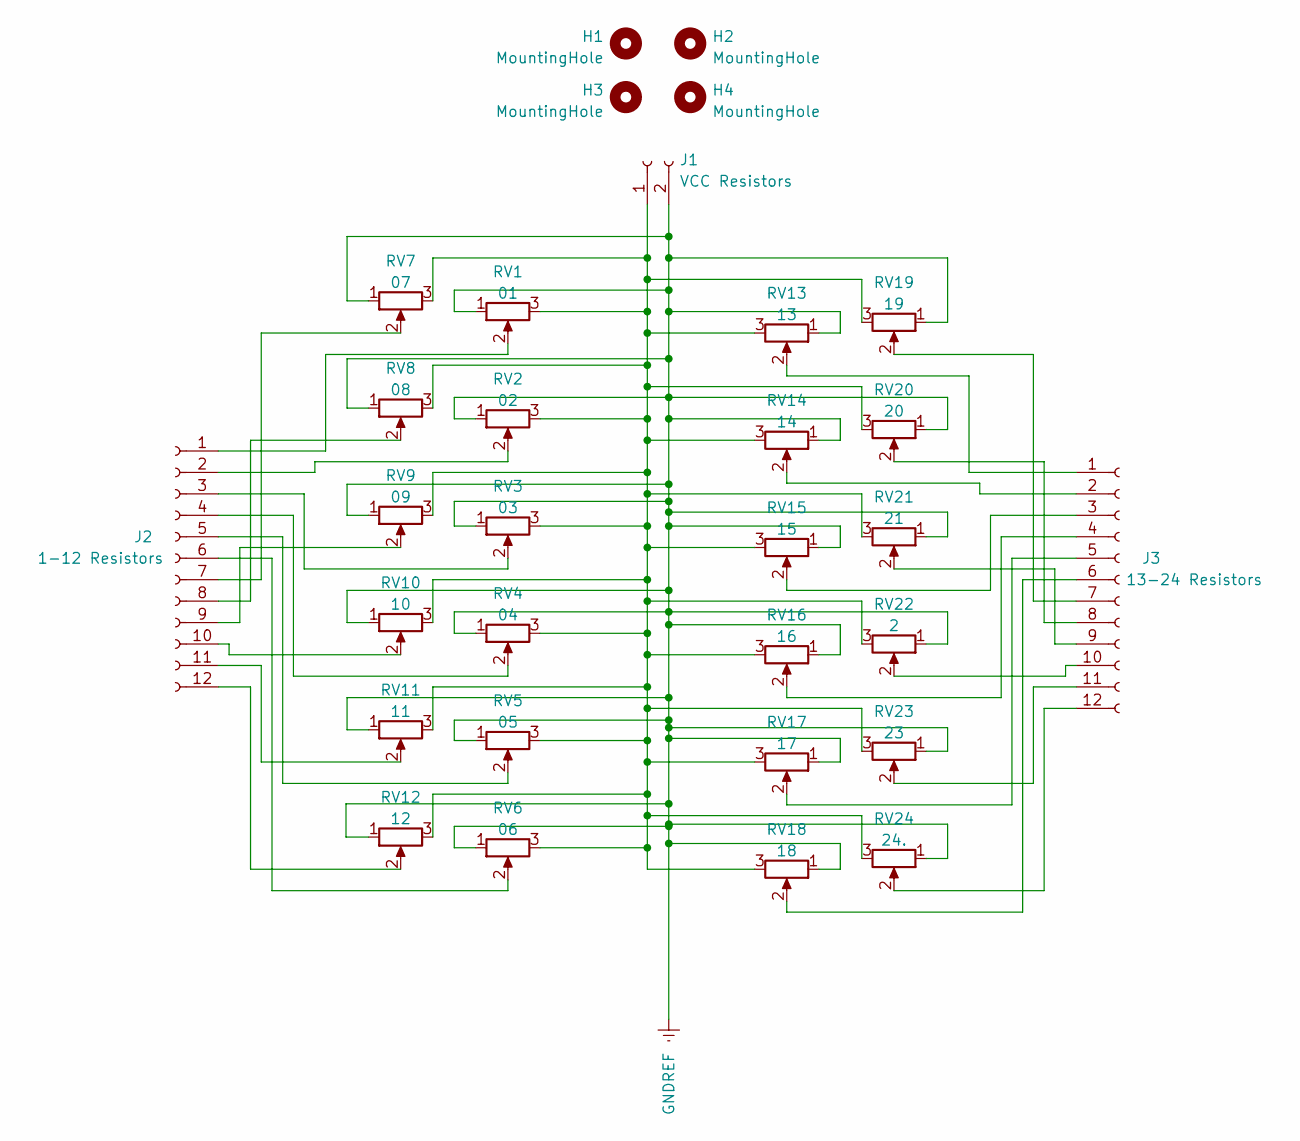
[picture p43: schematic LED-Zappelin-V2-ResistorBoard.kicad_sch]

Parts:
H1, H2, H3, H4: MountingHole; MountingHole_3mm
J1: VCC Resistors; JST_XH_S2B-XH-A-1_1x02_P2.50mm_Horizontal
J2: 1-12 Resistors; JST_XH_S12B-XH-A_1x12_P2.50mm_Horizontal
J3: 13-24 Resistors; JST_XH_S12B-XH-A_1x12_P2.50mm_Horizontal
RV1: 01; Potentiometer_Vishay_43_Horizontal
RV2: 02; Potentiometer_Vishay_43_Horizontal
RV3: 03; Potentiometer_Vishay_43_Horizontal
RV4: 04; Potentiometer_Vishay_43_Horizontal
RV5: 05; Potentiometer_Vishay_43_Horizontal
RV6: 06; Potentiometer_Vishay_43_Horizontal
RV7: 07; Potentiometer_Vishay_43_Horizontal
RV8: 08; Potentiometer_Vishay_43_Horizontal
RV9: 09; Potentiometer_Vishay_43_Horizontal
RV10: 10; Potentiometer_Vishay_43_Horizontal
RV11: 11; Potentiometer_Vishay_43_Horizontal
RV12: 12; Potentiometer_Vishay_43_Horizontal
RV13: 13; Potentiometer_Vishay_43_Horizontal
RV14: 14; Potentiometer_Vishay_43_Horizontal
RV15: 15; Potentiometer_Vishay_43_Horizontal
RV16: 16; Potentiometer_Vishay_43_Horizontal
RV17: 17; Potentiometer_Vishay_43_Horizontal
RV18: 18; Potentiometer_Vishay_43_Horizontal
RV19: 19; Potentiometer_Vishay_43_Horizontal
RV20: 20; Potentiometer_Vishay_43_Horizontal
RV21: 21; Potentiometer_Vishay_43_Horizontal
RV22: 2; Potentiometer_Vishay_43_Horizontal
RV23: 23; Potentiometer_Vishay_43_Horizontal
RV24: 24.; Potentiometer_Vishay_43_Horizontal

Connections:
GNDREF: J1.2, RV1.1, RV2.1, RV3.1, RV4.1, RV5.1, RV6.1, RV7.1, RV8.1, RV9.1, RV10.1, RV11.1, RV12.1, RV13.1, RV14.1, RV15.1, RV16.1, RV17.1, RV18.1, RV19.1, RV20.1, RV21.1, RV22.1, RV23.1, RV24.1
unnamed: J1.1, RV1.3, RV2.3, RV3.3, RV4.3, RV5.3, RV6.3, RV7.3, RV8.3, RV9.3, RV10.3, RV11.3, RV12.3, RV13.3, RV14.3, RV15.3, RV16.3, RV17.3, RV18.3, RV19.3, RV20.3, RV21.3, RV22.3, RV23.3, RV24.3
unnamed: J2.1, RV1.2
unnamed: J2.2, RV2.2
unnamed: J2.3, RV3.2
unnamed: J2.4, RV4.2
unnamed: J2.5, RV5.2
unnamed: J2.6, RV6.2
unnamed: J2.7, RV7.2
unnamed: J2.8, RV8.2
unnamed: J2.9, RV9.2
unnamed: J2.10, RV10.2
unnamed: J2.11, RV11.2
unnamed: J2.12, RV12.2
unnamed: J3.1, RV13.2
unnamed: J3.2, RV14.2
unnamed: J3.3, RV15.2
unnamed: J3.4, RV16.2
unnamed: J3.5, RV17.2
unnamed: J3.6, RV18.2
unnamed: J3.7, RV19.2
unnamed: J3.8, RV20.2
unnamed: J3.9, RV21.2
unnamed: J3.10, RV22.2
unnamed: J3.11, RV23.2
unnamed: J3.12, RV24.2

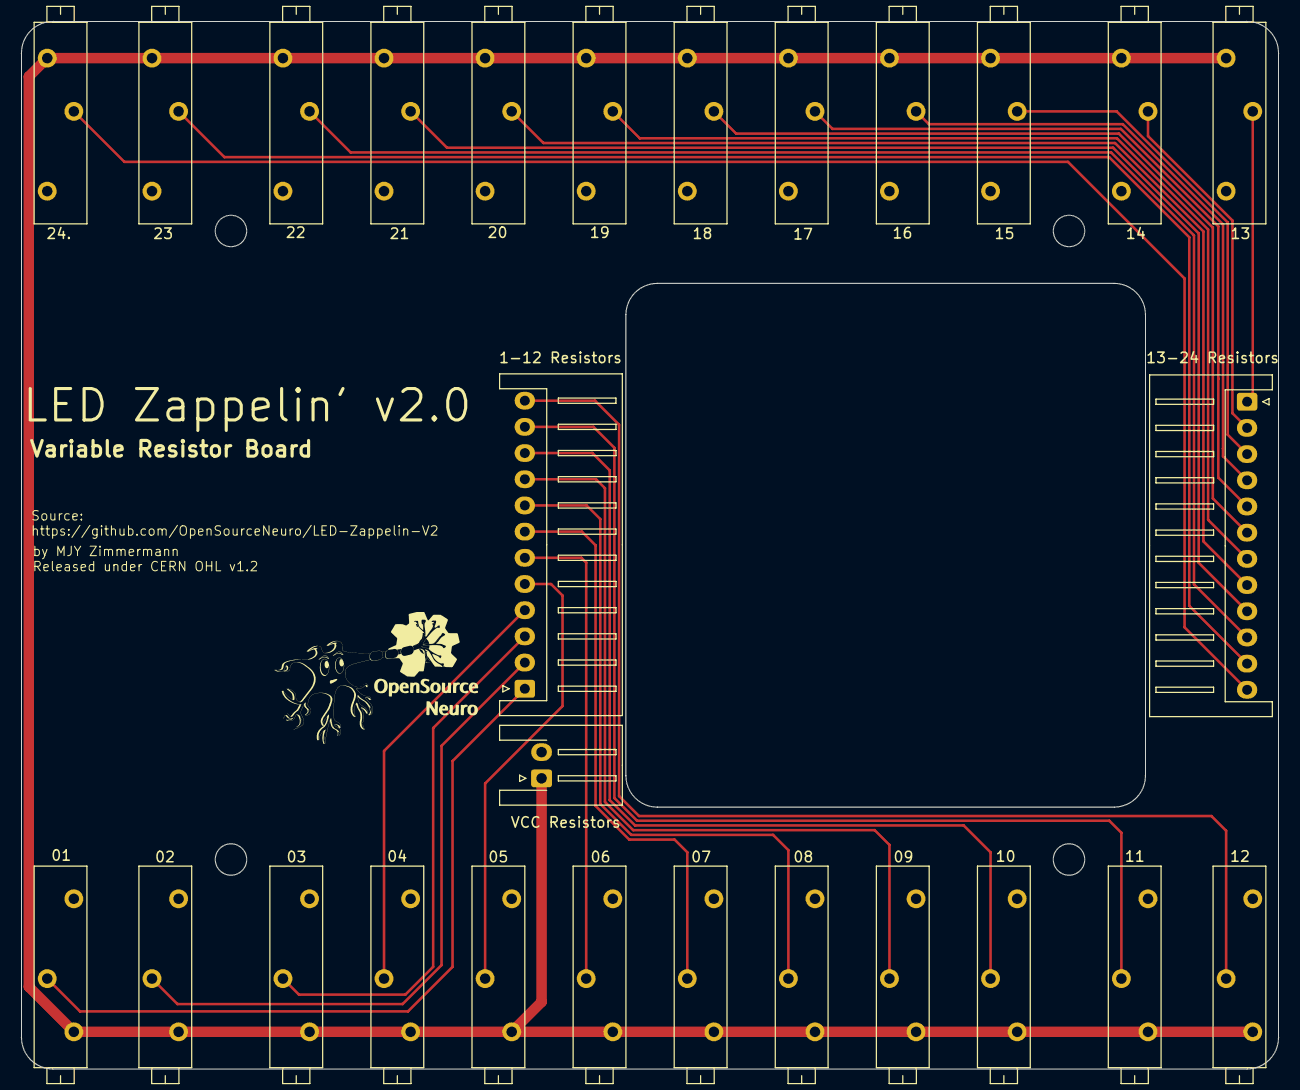
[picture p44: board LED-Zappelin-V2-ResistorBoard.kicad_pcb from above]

Board: 2 copper layers, 120.0 x 100.0 mm, 31 parts (0 on the bottom side), 26 nets.

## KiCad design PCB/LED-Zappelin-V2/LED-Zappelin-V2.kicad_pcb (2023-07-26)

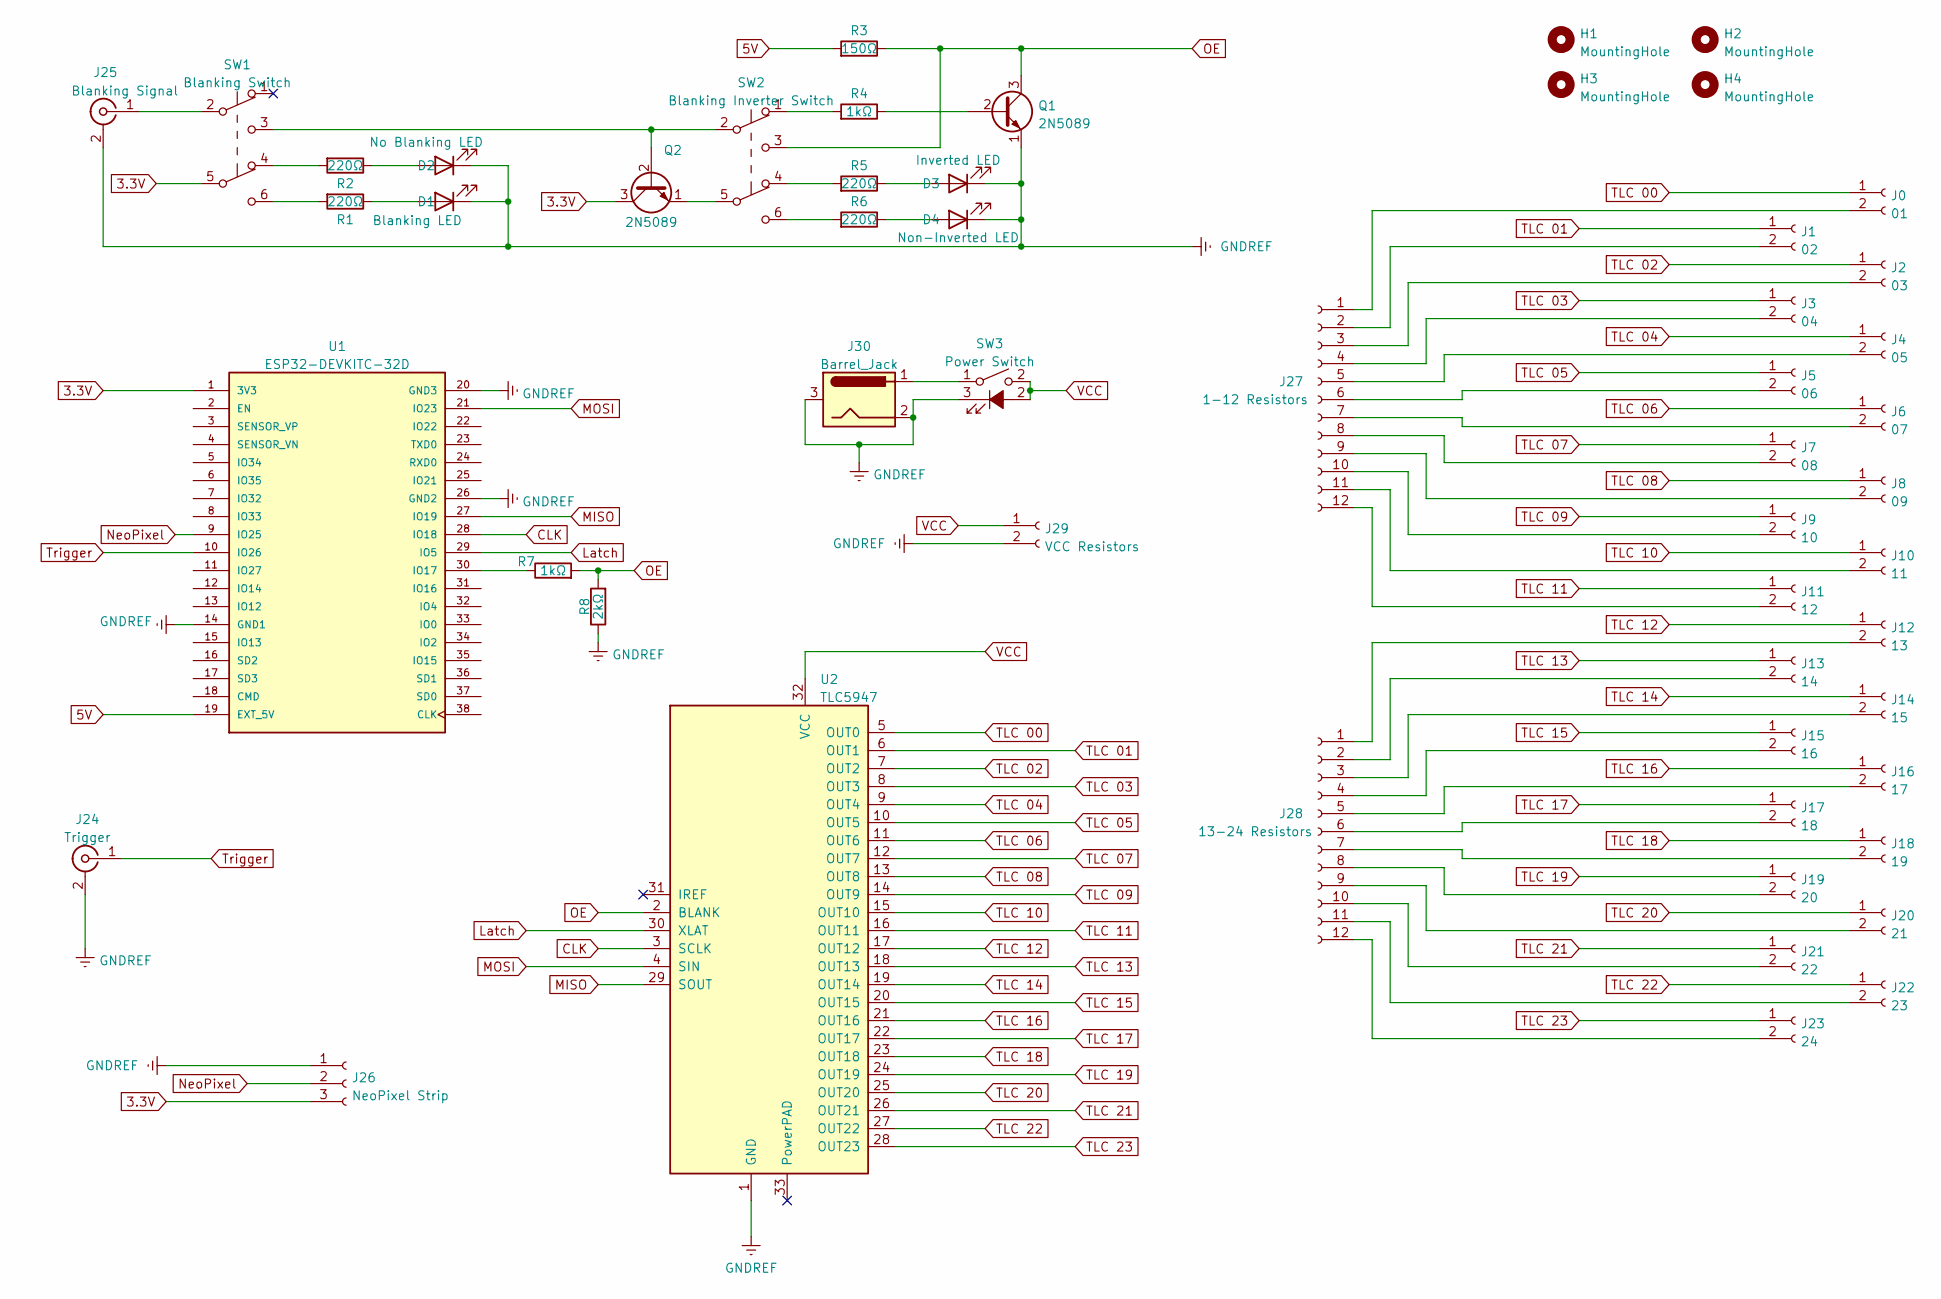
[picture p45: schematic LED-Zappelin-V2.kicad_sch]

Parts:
D1: Blanking LED; LED_D3.0mm
D2: No Blanking LED; LED_D3.0mm
D3: Inverted LED; LED_D3.0mm
D4: Non-Inverted LED; LED_D3.0mm
H1, H2, H3, H4: MountingHole; MountingHole_3mm
J0: 01; JST_XH_S2B-XH-A-1_1x02_P2.50mm_Horizontal
J1: 02; JST_XH_S2B-XH-A-1_1x02_P2.50mm_Horizontal
J2: 03; JST_XH_S2B-XH-A-1_1x02_P2.50mm_Horizontal
J3: 04; JST_XH_S2B-XH-A-1_1x02_P2.50mm_Horizontal
J4: 05; JST_XH_S2B-XH-A-1_1x02_P2.50mm_Horizontal
J5: 06; JST_XH_S2B-XH-A-1_1x02_P2.50mm_Horizontal
J6: 07; JST_XH_S2B-XH-A-1_1x02_P2.50mm_Horizontal
J7: 08; JST_XH_S2B-XH-A-1_1x02_P2.50mm_Horizontal
J8: 09; JST_XH_S2B-XH-A-1_1x02_P2.50mm_Horizontal
J9: 10; JST_XH_S2B-XH-A-1_1x02_P2.50mm_Horizontal
J10: 11; JST_XH_S2B-XH-A-1_1x02_P2.50mm_Horizontal
J11: 12; JST_XH_S2B-XH-A-1_1x02_P2.50mm_Horizontal
J12: 13; JST_XH_S2B-XH-A-1_1x02_P2.50mm_Horizontal
J13: 14; JST_XH_S2B-XH-A-1_1x02_P2.50mm_Horizontal
J14: 15; JST_XH_S2B-XH-A-1_1x02_P2.50mm_Horizontal
J15: 16; JST_XH_S2B-XH-A-1_1x02_P2.50mm_Horizontal
J16: 17; JST_XH_S2B-XH-A-1_1x02_P2.50mm_Horizontal
J17: 18; JST_XH_S2B-XH-A-1_1x02_P2.50mm_Horizontal
J18: 19; JST_XH_S2B-XH-A-1_1x02_P2.50mm_Horizontal
J19: 20; JST_XH_S2B-XH-A-1_1x02_P2.50mm_Horizontal
J20: 21; JST_XH_S2B-XH-A-1_1x02_P2.50mm_Horizontal
J21: 22; JST_XH_S2B-XH-A-1_1x02_P2.50mm_Horizontal
J22: 23; JST_XH_S2B-XH-A-1_1x02_P2.50mm_Horizontal
J23: 24; JST_XH_S2B-XH-A-1_1x02_P2.50mm_Horizontal
J24: Trigger; BNC_Socket_TYCO-AMP_LargePads
J25: Blanking Signal; BNC_Socket_TYCO-AMP_LargePads
J26: NeoPixel Strip; JST_XH_B3B-XH-A_1x03_P2.50mm_Vertical
J27: 1-12 Resistors; JST_XH_B12B-XH-A_1x12_P2.50mm_Vertical
J28: 13-24 Resistors; JST_XH_B12B-XH-A_1x12_P2.50mm_Vertical
J29: VCC Resistors; JST_XH_B2B-XH-A_1x02_P2.50mm_Vertical
J30: Barrel_Jack; BarrelJack_Horizontal
Q1, Q2: 2N5089; TO-92L_Inline_Wide
R1, R2, R5, R6: 220Ω; R_Axial_DIN0309_L9.0mm_D3.2mm_P15.24mm_Horizontal
R3: 150Ω; R_Axial_DIN0309_L9.0mm_D3.2mm_P15.24mm_Horizontal
R4, R7: 1kΩ; R_Axial_DIN0309_L9.0mm_D3.2mm_P15.24mm_Horizontal
R8: 2kΩ; R_Axial_DIN0309_L9.0mm_D3.2mm_P15.24mm_Horizontal
SW1: Blanking Switch; maxi_DPDT_Angled
SW2: Blanking Inverter Switch; maxi_DPDT_Angled
SW3: Power Switch; JST_XH_B3B-XH-A_1x03_P2.50mm_Vertical
U1: ESP32-DEVKITC-32D; MODULE_ESP32-DEVKITC-32D; PARTREV 4
U2: TLC5947; Maxi_TLC5947

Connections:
3.3V: J26.3, Q2.3 (C), SW1.5 (B), U1.1 (3V3)
5V: R3.2, U1.19 (EXT_5V)
CLK: U1.28 (IO18), U2.3 (SCLK)
GNDREF: D1.1 (K), D2.1 (K), D3.1 (K), D4.1 (K), J24.2 (Ext), J25.2 (Ext), J26.1, J29.2, J30.2, J30.3, Q1.1 (E), R8.1, SW3.3 (K), U1.14 (GND1), U1.20 (GND3), U1.26 (GND2), U2.1 (GND)
Latch: U1.29 (IO5), U2.30 (XLAT)
MISO: U1.27 (IO19), U2.29 (SOUT)
MOSI: U1.21 (IO23), U2.4 (SIN)
NeoPixel: J26.2, U1.9 (IO25)
unnamed: D1.2 (A), R1.1
unnamed: D2.2 (A), R2.1
unnamed: D3.2 (A), R5.1
unnamed: D4.2 (A), R6.1
unnamed: J0.2, J27.1
unnamed: J1.2, J27.2
unnamed: J2.2, J27.3
unnamed: J10.2, J27.11
unnamed: J11.2, J27.12
unnamed: J12.2, J28.1
unnamed: J13.2, J28.2
unnamed: J14.2, J28.3
unnamed: J15.2, J28.4
unnamed: J16.2, J28.5
unnamed: J17.2, J28.6
unnamed: J18.2, J28.7
unnamed: J19.2, J28.8
unnamed: J20.2, J28.9
unnamed: J21.2, J28.10
unnamed: J22.2, J28.11
unnamed: J23.2, J28.12
unnamed: J3.2, J27.4
unnamed: J4.2, J27.5
unnamed: J5.2, J27.6
unnamed: J6.2, J27.7
unnamed: J7.2, J27.8
unnamed: J8.2, J27.9
unnamed: J9.2, J27.10
unnamed: J30.1, SW3.1
unnamed: Q1.2 (B), R4.1
unnamed: Q2.1 (E), SW2.5 (B)
unnamed: Q2.2 (B), SW1.3 (C), SW2.2 (B)
unnamed: R4.2, SW2.1 (A)
unnamed: R5.2, SW2.4 (A)
unnamed: R6.2, SW2.6 (C)
unnamed: R7.1, U1.30 (IO17)
unnamed: J25.1 (In), SW1.2 (B)
unnamed: R2.2, SW1.4 (A)
unnamed: R1.2, SW1.6 (C)
OE: Q1.3 (C), R3.1, R7.2, R8.2, SW2.3 (C), U2.2 (BLANK)
TLC 00: J0.1, U2.5 (OUT0)
TLC 01: J1.1, U2.6 (OUT1)
TLC 02: J2.1, U2.7 (OUT2)
TLC 03: J3.1, U2.8 (OUT3)
TLC 04: J4.1, U2.9 (OUT4)
TLC 05: J5.1, U2.10 (OUT5)
TLC 06: J6.1, U2.11 (OUT6)
TLC 07: J7.1, U2.12 (OUT7)
TLC 08: J8.1, U2.13 (OUT8)
TLC 09: J9.1, U2.14 (OUT9)
TLC 10: J10.1, U2.15 (OUT10)
TLC 11: J11.1, U2.16 (OUT11)
TLC 12: J12.1, U2.17 (OUT12)
TLC 13: J13.1, U2.18 (OUT13)
TLC 14: J14.1, U2.19 (OUT14)
TLC 15: J15.1, U2.20 (OUT15)
TLC 16: J16.1, U2.21 (OUT16)
TLC 17: J17.1, U2.22 (OUT17)
TLC 18: J18.1, U2.23 (OUT18)
TLC 19: J19.1, U2.24 (OUT19)
TLC 20: J20.1, U2.25 (OUT20)
TLC 21: J21.1, U2.26 (OUT21)
TLC 22: J22.1, U2.27 (OUT22)
TLC 23: J23.1, U2.28 (OUT23)
Trigger: J24.1 (In), U1.10 (IO26)
VCC: J29.1, SW3.2, U2.32 (VCC)

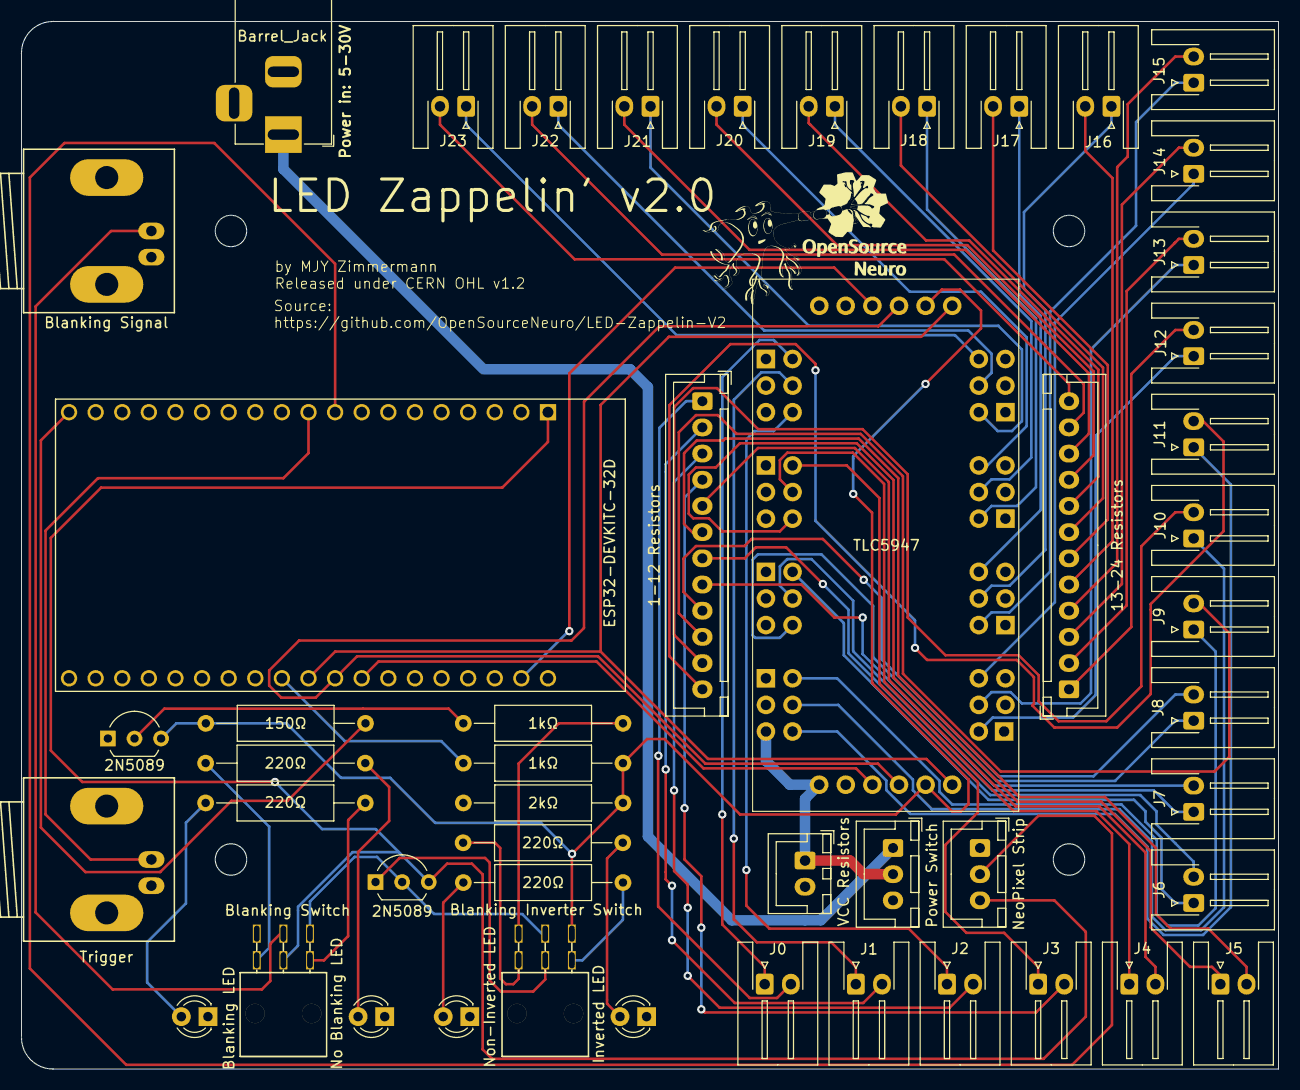
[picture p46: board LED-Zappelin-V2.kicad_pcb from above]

Board: 2 copper layers, 120.0 x 100.0 mm, 54 parts (0 on the bottom side), 74 nets.

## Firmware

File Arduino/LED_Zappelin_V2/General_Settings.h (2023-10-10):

/*          ---  General Settings  ---
*/
#include "LED_Values.h"                     // Include LED Values defined in the second tab
#include <SPI.h>                            // Include the arduino serial port interface library
#include "Adafruit_TLC5947.h"               // Include the Adafruit TLC5947 libvrary. For better result one may change the number of channel defined in the Adafruit_TLC5947.cpp library
#include <Adafruit_NeoPixel.h>


#define   MOSI           23                 // TLC SPI connection, Date Out
#define   MISO           19                 // TLC SPI connection,Data In 
#define   CLK            18                 // TLC SPI connection, Clock 
#define   latch          5                  // TLC Latch
#define   Blank          17                 // TLC Ouput Enable, Also Optional feature to prevent LED to light up when powering up the TLC board

#define   NeoPixel       25                 // NeoPixel pin
#define   NeoPixel_LED   16                 // Number of NeoPixel LEDs

#define   Trigger        26                 // Trigger channel must be connected to pin A0/DAC2


    Adafruit_TLC5947 tlc = Adafruit_TLC5947(1, CLK, MOSI, latch);
    //Adafruit_NeoPixel strip(NeoPixel_LED, NeoPixel, NEO_GRB + NEO_RGBW);
    Adafruit_NeoPixel strip(NeoPixel_LED, NeoPixel, NEO_GRB + NEO_KHZ800);


/* ----------------------------------------------------------------------------------*/
/* ------------------------------- Global Variables ---------------------------------*/

word           BaudRate      = 921600;      // Baud Rate speed
char           sCmd;                        // Serial monitor 
float          aNumber;
char           *arg;

bool           StimulusFlag = false;
bool           flag;
int            i;                           // Iteration loop factor
int            iLoop;
int            CurrentMicros;               // Current Microsecond clock
int            PreviousMicros;              // Microsecond clock stamp
int            DiffMicros;                  // Difference in microseconds between the clock and the stamp
int            tPreviousMicros;             // Microsecond clock stamp
int            tDiffMicros;                 // Difference in microseconds between the clock and the stamp
int            tdPreviousMicros;            // Microsecond clock stamp
int            tdDiffMicros;                // Difference in microseconds between the clock and the stamp
int            ResolutionMicros;            // Microseconds delay between two i iteration
int            PreAdaptMicros;              // Preadaptation period in microseconds
bool           PreAdaptationFlag;
bool           TriggerModeFlag;
int            TriggerMode;                 // Set the Trigger mode
int            TriggerArray[100];

int            t;                           // Trigger counter
int            td;                          // Trigger Pulse counter
int            tr;                          // TriggerTime array counter
bool           TriggerFlag = false;         // Trigger Flag
int            TriggerTime;                 // Lenght of the Trigger loop in ms 
int            TriggerDuration = 100000;    // Length of the Trigger signal in us 

int            brightness    = 100;         // NeoPixel brightness (max = 255)
int            l;                           // LED iteration factor


/* ----------------------------------------------------------------------------------*/
/* --------------------- LED Zappelion' initialising conditions ---------------------*/

void HardwareSettings(){
  
// Initialise the serial communication with PC
  Serial.begin(BaudRate);                      
  
// Initialise the Adafruit TLC driver 
  tlc.begin();
  tlc.write();  

// Initialise the Neopixel Strip
  if (OldNeopixel == true){
    Adafruit_NeoPixel strip(NeoPixel_LED, NeoPixel, NEO_GRB + NEO_KHZ800);
  }
  strip.begin();           
  strip.show();                    // Turn OFF all pixels ASAP
  strip.setBrightness(brightness); // Set NeoPixel brightness 

// Set pins
  pinMode(Trigger, OUTPUT);  
  digitalWrite(Trigger, LOW);  
  pinMode(Blank, INPUT);
  digitalWrite(Blank, HIGH);
  pinMode(13,OUTPUT);
  digitalWrite(Trigger, LOW); 

// Initialise parameters
  l = 0;
  t = 0;
  td = 0;
  TriggerFlag = false;
  CurrentMicros = 0;
  PreviousMicros = 0;
  DiffMicros = 0;
  tPreviousMicros = 0;
  tDiffMicros = 0;
  tdPreviousMicros = 0;
  flag = true;
}

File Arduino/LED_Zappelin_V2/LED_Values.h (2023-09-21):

boolean   OldNeopixel  = true;              // Set Neopixel stick version (RGB vs RGBW)
int       nLED         = 12;                // Total number of LED 

/* ----------------------------------------------------------------------------------*/
/* ------------------------------ LED Wavelength (nm) -------------------------------*/

const int Wavelength01 = 365;
const int Wavelength02 = 366;
const int Wavelength03 = 385;
const int Wavelength04 = 405;
const int Wavelength05 = 420;
const int Wavelength06 = 475;
const int Wavelength07 = 490;
const int Wavelength08 = 525;
const int Wavelength09 = 543;
const int Wavelength10 = 570;
const int Wavelength11 = 610;
const int Wavelength12 = 625;

int Wavelength_Array[] {Wavelength01,Wavelength02,Wavelength03,Wavelength04,Wavelength05,Wavelength06,Wavelength07,Wavelength08,Wavelength09,Wavelength10,Wavelength11,Wavelength12};


/* ----------------------------------------------------------------------------------*/
/* ----------------- Max LED power ( to be set during calibration) ------------------*/

const int max_LED01 = 4095;  
const int max_LED02 = 4095;  
const int max_LED03 = 4095;  
const int max_LED04 = 4095;  
const int max_LED05 = 4095;  
const int max_LED06 = 4095;  
const int max_LED07 = 4095;  
const int max_LED08 = 4095;  
const int max_LED09 = 4095;  
const int max_LED10 = 4095;  
const int max_LED11 = 4095;  
const int max_LED12 = 4095;  

int LEDPower_Array[] = {max_LED01, max_LED02, max_LED03, max_LED04, max_LED05, max_LED06, max_LED07, max_LED08, max_LED09, max_LED10, max_LED11, max_LED12 };


/* ----------------------------------------------------------------------------------*/
/* ----------------------------  Max Intensity LED power  ---------------------------*/

int max_LED_Power = 100;

const int max01 = max_LED_Power;  // LED maximum intensity 1
const int max02 = max_LED_Power;  // LED maximum intensity 2
const int max03 = max_LED_Power;  // LED maximum intensity 3
const int max04 = max_LED_Power;  // LED maximum intensity 4
const int max05 = max_LED_Power;  // LED maximum intensity 5
const int max06 = max_LED_Power;  // LED maximum intensity 6
const int max07 = max_LED_Power;  // LED maximum intensity 7
const int max08 = max_LED_Power;  // LED maximum intensity 8
const int max09 = max_LED_Power;  // LED maximum intensity 9
const int max10 = max_LED_Power;  // LED maximum intensity 10
const int max11 = max_LED_Power;  // LED maximum intensity 11
const int max12 = max_LED_Power;  // LED maximum intensity 12

int LEDPower_Array2[] = {max01, max02, max03, max04, max05, max06, max07, max08, max09, max10, max11, max12};


/* ----------------------------------------------------------------------------------*/
/* ----------------------------------- LED arrays -----------------------------------*/

int led01 = 0;   // Define 1st Channel
int led02 = 1;   // Define 2nd Channel
int led03 = 2;   // Define 3rd Channel
int led04 = 3;   // Define 4th Channel
int led05 = 4;   // Define 5th Channel
int led06 = 5;   // Define 6th Channel
int led07 = 6;   // Define 7th Channel
int led08 = 7;   // Define 8th Channel
int led09 = 8;   // Define 9th Channel
int led10 = 9;   // Define 10th Channel
int led11 = 10;  // Define 11th Channel
int led12 = 11;  // Define 12th Channel

int LED_Array[] = {led01, led02, led03, led04, led05, led06, led07, led08, led09, led10, led11, led12};


/* ----------------------------------------------------------------------------------*/
/* ------------------------ Stimuli relative LED power (%) --------------------------*/

int LED1_Power = 0;
int LED2_Power = 0;
int LED3_Power = 0;
int LED4_Power = 0;
int LED5_Power = 0;
int LED6_Power = 0;
int LED7_Power = 0;
int LED8_Power = 0;
int LED9_Power = 0;
int LED10_Power = 0;
int LED11_Power = 0;
int LED12_Power = 0;

int LEDPower[] = {LED1_Power, LED2_Power, LED3_Power, LED4_Power, LED5_Power, LED6_Power, LED7_Power, LED8_Power, LED9_Power, LED10_Power, LED11_Power, LED12_Power};

/* ----------------------------------------------------------------------------------*/
/* -------------------------------- Neopixel HSV hue --------------------------------*/

int bits = 65535;
int hsv_hue1;
int hsv_hue2;
int hsv_hue3;
int hsv_hue4;
int hsv_hue5;
int hsv_hue6;
int hsv_hue7;
int hsv_hue8;
int hsv_hue9;
int hsv_hue10;
int hsv_hue11;
int hsv_hue12;


int hsv_hue_Array[] = {hsv_hue1, hsv_hue2, hsv_hue3, hsv_hue4, hsv_hue5, hsv_hue6, hsv_hue7, hsv_hue8, hsv_hue9, hsv_hue10, hsv_hue11, hsv_hue12};


/* ----------------------------------------------------------------------------------*/
/* ---------------------------- Neopixel HSV saturation -----------------------------*/

int hsv_sat = 255;

int hsv_sat1 = hsv_sat;
int hsv_sat2 = hsv_sat;
int hsv_sat3 = hsv_sat;
int hsv_sat4 = hsv_sat;
int hsv_sat5 = hsv_sat;
int hsv_sat6 = hsv_sat;
int hsv_sat7 = hsv_sat;
int hsv_sat8 = hsv_sat;
int hsv_sat9 = hsv_sat;
int hsv_sat10 = hsv_sat;
int hsv_sat11 = hsv_sat;
int hsv_sat12 = hsv_sat;

int hsv_sat_Array[] = {hsv_sat1, hsv_sat2, hsv_sat3, hsv_sat4, hsv_sat5, hsv_sat6, hsv_sat7, hsv_sat8, hsv_sat9, hsv_sat10, hsv_sat11, hsv_sat12};


/* ----------------------------------------------------------------------------------*/
/* ------------------------------- Neopixel HSV value -------------------------------*/

int hsv_val = 100;

int hsv_val1 = hsv_val;
int hsv_val2 = hsv_val;
int hsv_val3 = hsv_val;
int hsv_val4 = hsv_val;
int hsv_val5 = hsv_val;
int hsv_val6 = hsv_val;
int hsv_val7 = hsv_val;
int hsv_val8 = hsv_val;
int hsv_val9 = hsv_val;
int hsv_val10 = hsv_val;
int hsv_val11 = hsv_val;
int hsv_val12 = hsv_val;

int hsv_val_Array[] = {hsv_val1, hsv_val2, hsv_val3, hsv_val4, hsv_val5, hsv_val6, hsv_val7, hsv_val8, hsv_val9, hsv_val10, hsv_val11, hsv_val12};



void SetWavelength(){
  for (int i = 0; i <= nLED-1; i++) {
    float Wave = Wavelength_Array[i];

    // Convert wavelength into RGB
    float attenuation;
    float rr;
    float gg;
    float bb;

    if (Wave <= 365){
      Wave = 365;
    }
    if (Wave >= 780){
      Wave = 780;
    }

    if (Wave>=365 && Wave<440){
      attenuation = 0.3 + 0.7 * (Wave - 365) / (440 - 365);
      rr = -(Wave - 440) / (440 - 365) * attenuation;
      gg = 0.0;
      bb = attenuation;
    }
    else if (Wave>=440 && Wave<490){
      rr = 0.0;
      gg = (Wave - 440) / (490 - 400);
      bb = 1.0;
    }
    else if (Wave>=490 && Wave<510){
      rr = 0.0;
      gg = 1.0;
      bb = (Wave - 510) / (510 - 490);
    }
    else if (Wave>=510 && Wave<580){
      rr = (Wave - 510) / (580 - 510);
      gg = 1.0;
      bb = 0.0;
    }
    else if (Wave>=580 && Wave<645){
      rr = 1.0;
      gg = -(Wave - 645) / (645 - 580);
      bb = 0.0;
    }
    else if (Wave>=645 && Wave<780){
      attenuation = 0.3 + 0.7 * (780 - Wave) / (780 - 645);
      rr = attenuation;
      gg = 0.0;
      bb = 0.0;
    }
    else {
      rr = 0.0;
      gg = 0.0;
      bb = 0.0;
    }

    // Convert RGB to Hue
    float Hue;
    int   HSV_Hue;
    float maxC = max(max(rr,gg),bb);
    float minC = min(min(rr,gg),bb);
    float rangeC = maxC - minC;

    float rC = (maxC-rr) / rangeC;
    float gC = (maxC-gg) / rangeC;
    float bC = (maxC-bb) / rangeC;

    if (minC == maxC){
      Hue = 0;
    }
    else if (rr == maxC){
      Hue = bC - gC;
    }
    else if (gg == maxC){
      Hue = 2.0 + rC - bC;
    }
    else {
      Hue = 4.0 + gC - rC;
    }
    Hue = (Hue / 6.0);
    if (OldNeopixel == false){
      HSV_Hue = round(bits - (Hue * bits));
    }
    if (OldNeopixel == true){
      HSV_Hue = round(Hue * bits);
    }
    hsv_hue_Array[i] = HSV_Hue;
  }
}

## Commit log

2023-07-26 First commit - 3D
    [Back.dxf, Bottom.dxf, Front.dxf, LED-Zappelin V2 - Chrolis.scad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]
2023-07-26 First commit - Arduino
2023-07-26 First commit - PCB
    [LED-Zappelin-V2-B_Cu.gbr, LED-Zappelin-V2-B_Mask.gbr, LED-Zappelin-V2-B_Paste.gbr, LED-Zappelin-V2-B_Silkscreen.gbr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]
2023-07-26 First commit - GUI
    [Chrolis_AmpChirp5Hz.csv, Chrolis_LinChirp10Hz.csv, Chrolis_LinChirp15Hz.csv, Chrolis_LinChirp5Hz.csv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]
2023-08-16 Update Casing files
    [Back.dxf, Bottom.dxf, Front.dxf, LED-Zappelin V2 - Chrolis.scad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]
2023-08-16 Create 3D files
    [1_LED_Holder.stl, 2_LED_Holder.stl, 3_LED_Holder.stl, 4_LED_Holder.stl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]
2023-08-16 add LED_Zappelin.exe
2023-08-17 Create Opsin-LED Spectra.png
2023-08-23 Update LED-Zappelin V2.scad
    [LED-Zappelin V2.scad]
2023-08-24 Create LED-Zappelin V2 - Chrolis_Back.stl
    [LED-Zappelin V2 - Chrolis_Back.stl]
2023-08-24 Create LED-Zappelin V2 - Chrolis_Bottom.stl
    [LED-Zappelin V2 - Chrolis_Bottom.stl]
2023-08-24 Create LED-Zappelin V2 - Chrolis_Front.stl
    [LED-Zappelin V2 - Chrolis_Front.stl]
2023-08-24 Create LED-Zappelin V2 - Chrolis_Left.stl
    [LED-Zappelin V2 - Chrolis_Left.stl]
2023-08-24 Create LED-Zappelin V2 - Chrolis_Right.stl
    [LED-Zappelin V2 - Chrolis_Right.stl]
2023-08-24 Create LED-Zappelin V2 - Chrolis_Top.stl
    [LED-Zappelin V2 - Chrolis_Top.stl]
2023-08-25 Update Stimuli
    [Chrolis_AmplitudeChirp_3Hz.csv, Chrolis_ExponentialChirp_10Hz.csv, Chrolis_LinearChirp_10Hz.csv, Chrolis_OfficialNoise.csv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]
2023-08-25 Update Arduino
2023-08-25 update GUI
    [Chrolis_AmpChirp5Hz.csv, Chrolis_LinChirp10Hz.csv, Chrolis_LinChirp15Hz.csv, Chrolis_LinChirp5Hz.csv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]
2023-10-10 update Arduinos
2023-10-10 update notebooks
    [Chrolis_AmplitudeChirp_3Hz.csv, Chrolis_ExponentialChirp_10Hz.csv, Chrolis_OnOff_All_3sec.csv]
2023-11-01 update Arduino libraries
2023-11-07 update PCB
2023-11-10 update board for chrolis
    This update adds a voltage regulator to the board, as well as a connection to an external power supply. Footprints have been moved around so that only two sides of the board have connectors.
    [LED-Zappelin-V2-Chrolis-B_Cu.gbr, LED-Zappelin-V2-Chrolis-B_Mask.gbr, LED-Zappelin-V2-Chrolis-B_Paste.gbr, LED-Zappelin-V2-Chrolis-B_Silkscreen.gbr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]
2023-11-11 update PCB
    Previous modifications were kept, transistor Q2 was rerouted to sw1 pin6, all power line are now linked to external 5v power supply.
    PCB was rearranged to accommodate box equipment. The neopixel strip for example requires 110mm +some tolerance on one side
    [LED-Zappelin-V2-Chrolis-B_Cu.gbr, LED-Zappelin-V2-Chrolis-B_Mask.gbr, LED-Zappelin-V2-Chrolis-B_Paste.gbr, LED-Zappelin-V2-Chrolis-B_Silkscreen.gbr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]
